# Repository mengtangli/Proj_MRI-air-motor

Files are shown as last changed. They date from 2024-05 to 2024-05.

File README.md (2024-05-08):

# Proj_MRI-air-motor
# readme

% ========================== GENERAL INFO ============================== %

 - Authors: Zhijie Pan & Mengtang Li, Ph.D.
 - Institution: Sun Yat-Sen University, China.
 - Date: 2024 05 08 (first release)

 Description:
  - Please read the published Journal ariticle for more info: Pan, Z., et al. Cornerstone for MRI-compatible robots: A continuous pneumatic actuator
with easy-to-connect prismatic/revolute and bidirectional encoder modules, MEASRUEMENT, 2024. https://doi.org/10.1016/j.measurement.2024.114685
  - Supp. Vid can be found at: https://www.youtube.com/watch?v=GabAmfBLwVU&t=7s
  - This guihub repo contains the open sourced CAD files for the proposed MRI-compatible pneumatic motor, and PCB files for the optical fiber encoder (will update later).

% ========================== Detailed INFO - ENG ============================== %
## Three-dimensional Design Software and Versions

SolidWorks Version: 2019 and above. Files cannot be opened in versions lower than this.

## Modification of Part Dimensions

Models in the `Vanetype_AirMotor_V2` folder are designed with perfect dimensions. However, due to manufacturing tolerances and assembly requirements, some parts need slight modifications.

Models in the `Vanetype_AirMotor_V2_prototype` folder account for manufacturing tolerances and assembly requirements. However, their accuracy depends on the precision of the 3D printer or CNC machine used. The "Parts list" file provides the types and quantities of parts needed to assemble the prototype.

The table below indicates key modifications made to parts in this prototype for reference only. Actual modifications should be based on the precision of your 3D printer and CNC machine.

| Part Name          |                           Modifications                           |
| :----------------- | :---------------------------------------------------------------: |
| output_shaft       |      Reduced the cylinder diameter for positioning planetary gears by 0.2mm, decreased disk thickness by 0.1mm      |
| carrier_thick      | Reduced the cylinder diameter for positioning planetary gears by 0.2mm, decreased disk thickness by 0.1mm, reduced thickness of middle gear by 0.2mm |
| carrier_thin       | Reduced the cylinder diameter for positioning planetary gears by 0.2mm, decreased disk thickness by 0.1mm, reduced thickness of middle gear by 0.2mm |
| input_gear         |                        Reduced thickness by 0.2mm                         |
| reducer_cover_back |                      Decreased disk thickness by 0.5mm                       |
| rotor              |          Increased blade slot width by 0.15mm, shortened output shaft length by 0.2mm           |
| motor_back_cover   |               Increased outer diameter of guide rail by 0.2mm, decreased inner diameter by 0.1mm               |
| motor_front_cover  |               Increased outer diameter of guide rail by 0.2mm, decreased inner diameter by 0.1mm               |
| motor_housing      |           Increased overall thickness by 0.3mm, enlarged diameter of middle through-hole by 0.2mm           |
| encoder_disk       |                      Reduced overall thickness by 0.2mm                       |

## Notes

- Due to frequent relative sliding between vanes, rotor, and two covers (motor_back_cover and motor_front_cover), it's recommended to use materials with low friction coefficients for these parts. Teflon material was used here, machined through CNC. Ensure smooth movement between these parts and apply plastic-specific lubricant if necessary.
- The sealing of the motor chamber significantly affects motor output performance. Here, two O-ring rubber seals are used to ensure the motor housing remains airtight.
- When the output shaft of the reducer experiences axial force, it significantly affects the torque performance of the actuator, as mentioned in the paper showing the performance graph with the linear module. This is likely due to the structure of the reducer, where axial pressure increases the resistance experienced by the input gear of the reducer, directly affecting rotor rotation.
- Plastic-specific lubricant should be added inside the reducer to reduce friction.
- Experimental testing revealed that the actuator prototype does not initially perform at its best. As the testing progresses and internal parts wear in over time, the performance of the actuator prototype improves.

% ========================== Detailed INFO - CHN ============================== %
## 三维制图软件及版本

SolidWorks版本：2019及以上，低于此版本则打不开SW源文件。

## 零件尺寸修改

`Vanetype_AirMotor_V2`文件夹中的模型为完美尺寸模型，由于需要考虑制造误差以及配合公差，因此需要对一些零件稍作修改。

`Vanetype_AirMotor_V2_prototype` 文件夹中的模型考虑了制造误差以及配合公差，由于3D打印和CNC加工的精度取决于所操作的机器，因此仅作参考。`Parts list`文件给出了制作样机所需要零件的种类及数量。

下表列举了本样机中的零件已修改了哪些关键的地方，仅作参考，需要根据自己的3D打印机和CNC机器的制造精度进行修改。

| 零件名称           |                           修改选型                           |
| :----------------- | :----------------------------------------------------------: |
| output_shaft       |      定位行星齿轮的圆柱直径减小0.2mm，圆盘厚度减小0.1mm         |
| carrier_thick      | 定位行星齿轮的圆柱直径减小0.2mm，圆盘厚度减小0.1mm，中间齿轮厚度减小0.2mm |
| carrier_thin       | 定位行星齿轮的圆柱直径减小0.2mm，圆盘厚度减小0.1mm，中间齿轮厚度减小0.2mm |
| input_gear         |                        厚度减小0.2mm                         |
| reducer_cover_back |                      圆盘厚度减小0.5mm                       |
| rotor              |          叶片槽宽度增加0.15mm，输出轴长度缩短0.2mm             |
| motor_back_cover   |               导轨外径增加0.2mm，内径减小0.1mm               |
| motor_front_cover  |               导轨外径增加0.2mm，内径减小0.1mm               |
| motor_housing      |           整体厚度增加0.3mm，中间通孔直径增大0.2mm            |
| encoder_disk       |                      整体厚度减小0.2mm                       |

## 注意事项

- 由于叶片 (vane) 与转子 (rotor)、叶片 (vane) 与两个封盖 (motor_back_cover and motor_front_cover) 之间存在频繁的相对滑动，因此建议使用摩擦系数低的材料制作这些零件，这里使用了特氟龙 (teflon)材料通过CNC加工得到。需要确保这些零件之间能够顺畅地滑动，必要时可添加塑料专用润滑脂。
- 马达 (motor) 腔室的密封性对马达的输出性能影响较大，这里通过两个O型弹性橡胶圈进行密封，确保马达外壳不会漏气。
- 减速器的输出轴受到轴向力时，会显著影响执行器的扭矩性能的输出，这点论文中在展示搭配直线模块性能图时有提及到。原因猜测应该与减速器的结构有关，受到轴向压力时，会增大减速器的输入齿轮所受到的阻力，从而直接影响转子转动。
- 减速器内部需要添加塑料专用的润滑脂，从而降低摩擦。
- 实验测试时发现，刚装配完成执行器样机并没有发挥出最好的性能，随着测试进行，内部零件磨合一段时间后，执行器样机的性能会提升。

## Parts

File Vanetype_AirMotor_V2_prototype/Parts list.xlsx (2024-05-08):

 | 零件名称 | 数量 | 备注
Motor | motor_back_cover | 1
 | rotor | 1
 | vane | 5
 | motor_housing | 1
 | motor_front_cover | 1
Encoder | encoder_support | 1
 | encoder_housing | 1
 | encoder_disk | 1
Reducer | reducer_housing | 1
 | reducer_housing_two-stage | 1
 | input_gear | 2
 | carrier_thin | 1
 | planet_gear_thin | 9
 | carrier_thick | 2
 | output_shaft | 2
 | planet_gear_thick | 6
 | reducer_cover_front | 2
 | reducer_cover_back | 2
Linear module | linear_main_housing | 1
 | linear_output_shaft | 1
 | rotation_screw | 1
Standard component | 塑料轴承
 | 5*11*3 | 2
 | 8*16*4 | 2
 | 3*7*2 | 1
 | 其他
 | Φ42*1.5 O型密封圈 | 2
 | M3*40螺丝 | 4
 | M3*12螺丝 | 4
 | M3*25螺丝 | 4
 | M2*12螺丝 | 4
 | M2.5*12尼龙平头螺丝 | 3
 | M2.5尼龙螺母 | 3
 | M3螺母 | 8

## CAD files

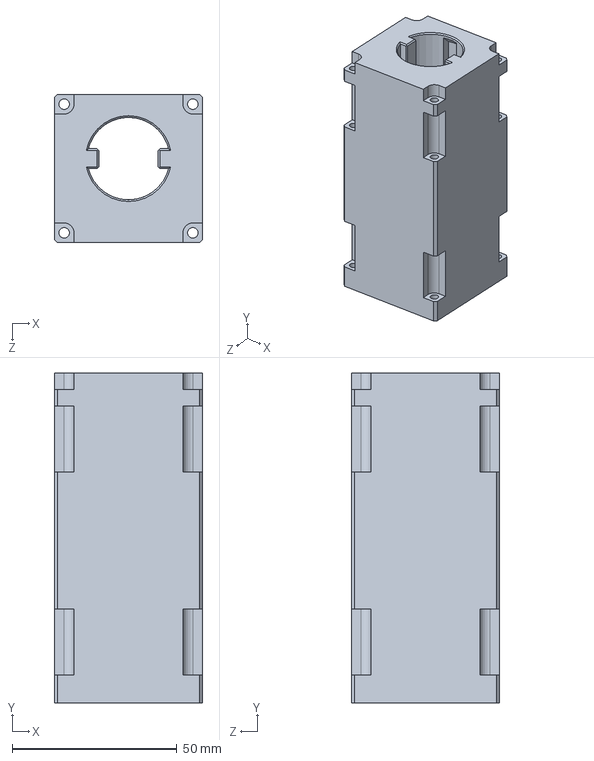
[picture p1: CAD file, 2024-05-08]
Vanetype_AirMotor_V2/Linear_module/linear_main_housing.SLDPRT
45.0 x 100.0 x 45.0 mm

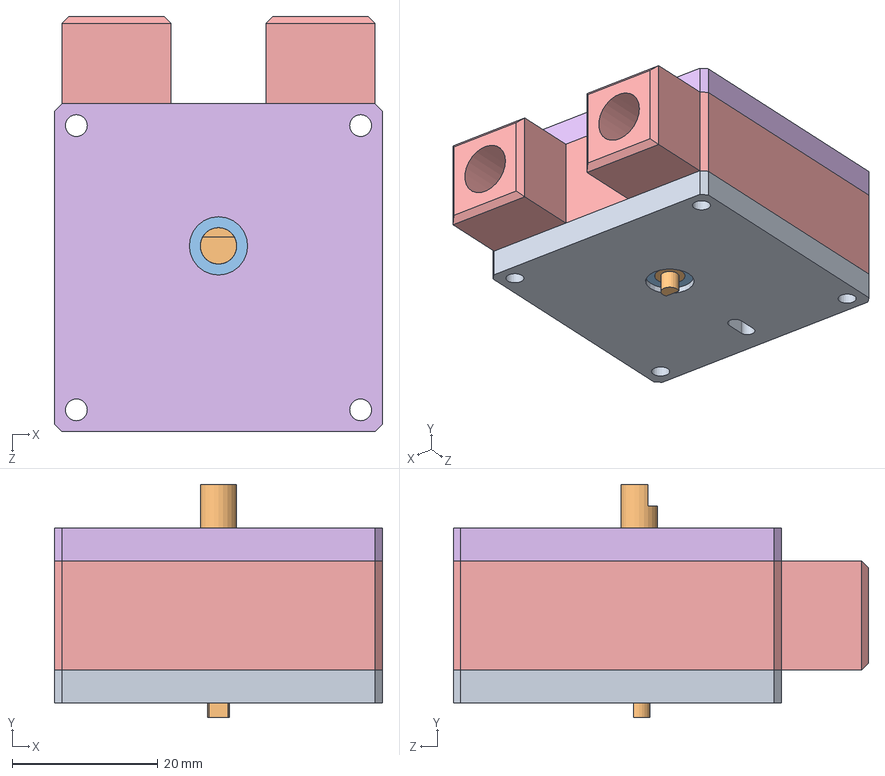
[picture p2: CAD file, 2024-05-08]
Vanetype_AirMotor_V2/Motor/motor.SLDASM
45.0 x 32.0 x 57.0 mm
motor_back_cover
rotor
5-11-3bearing x 2
vane x 5
motor_housing
motor_front_cover
sealing_ring x 2

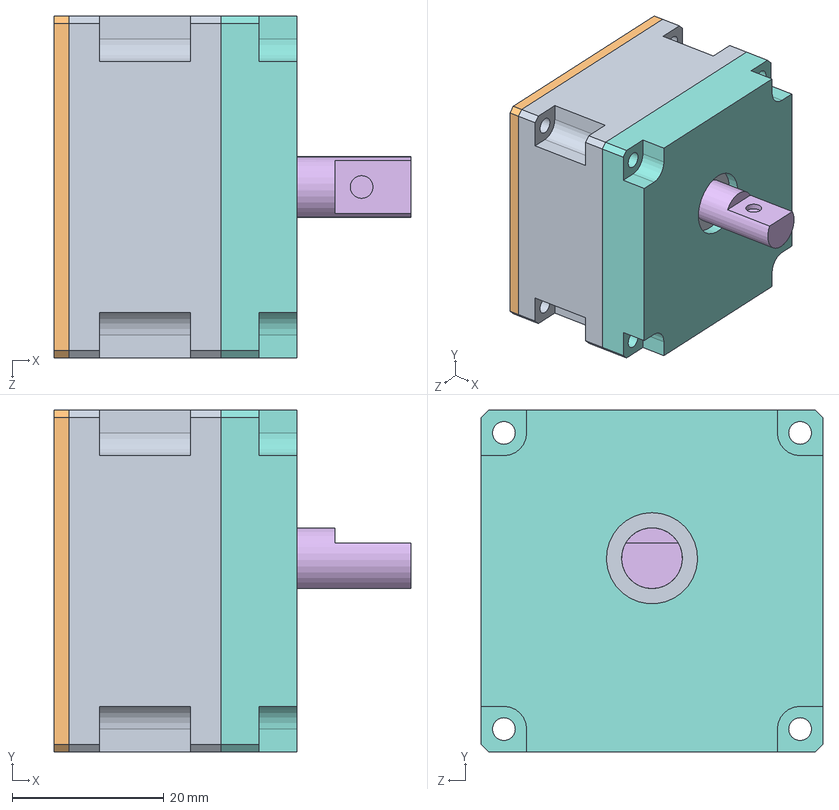
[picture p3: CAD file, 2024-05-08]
Vanetype_AirMotor_V2/Reducer/reducer.SLDASM
47.0 x 45.0 x 45.0 mm
reducer_housing
input_gear
carrier_thin
planet_gear_thin x 6
carrier_thick
output_shaft
planet_gear_thick x 3
reducer_cover_front
8-16-4bearing
reducer_cover_back

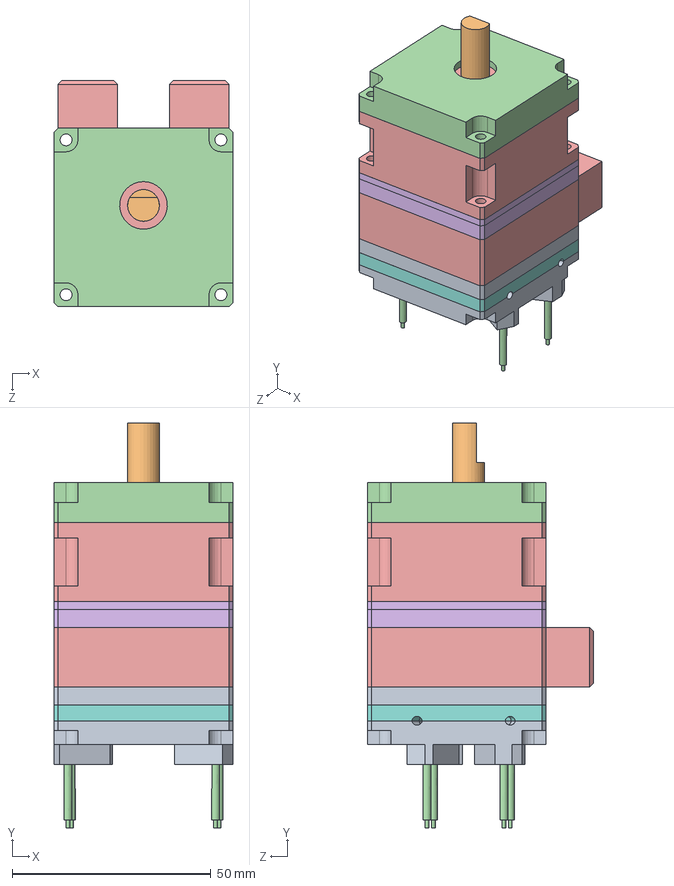
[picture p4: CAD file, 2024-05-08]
Vanetype_AirMotor_V2/Rotary_actuator.SLDASM
45.0 x 102.0 x 57.0 mm
motor_back_cover
rotor
5-11-3bearing x 2
vane x 5
motor_housing
motor_front_cover
sealing_ring x 2
encoder_support
encoder_housing
encoder_disk
3-7-2bearing
optical_fiber x 4
reducer_housing
input_gear
carrier_thin
planet_gear_thin x 6
carrier_thick
output_shaft
planet_gear_thick x 3
reducer_cover_front
8-16-4bearing
reducer_cover_back

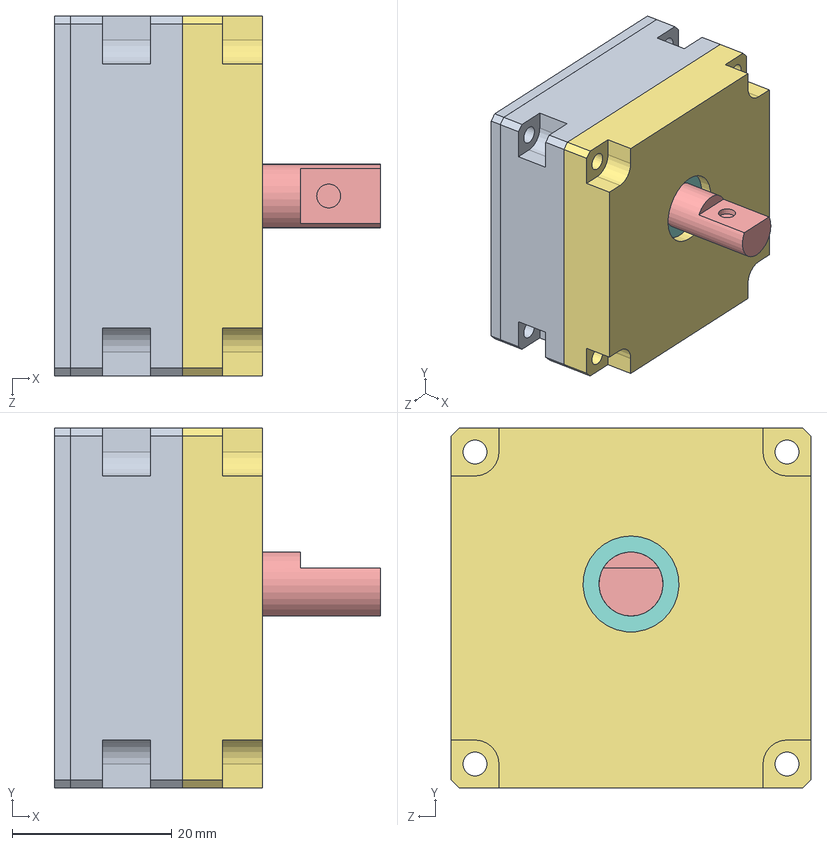
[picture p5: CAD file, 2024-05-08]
Vanetype_AirMotor_V2_prototype/Reducer/reducer_two-stage.SLDASM
40.8 x 45.0 x 45.0 mm
reducer_housing_two-stage
input_gear
carrier_thick
planet_gear_thin x 3
output_shaft
planet_gear_thick x 3
reducer_cover_front
8-16-4bearing
reducer_cover_back

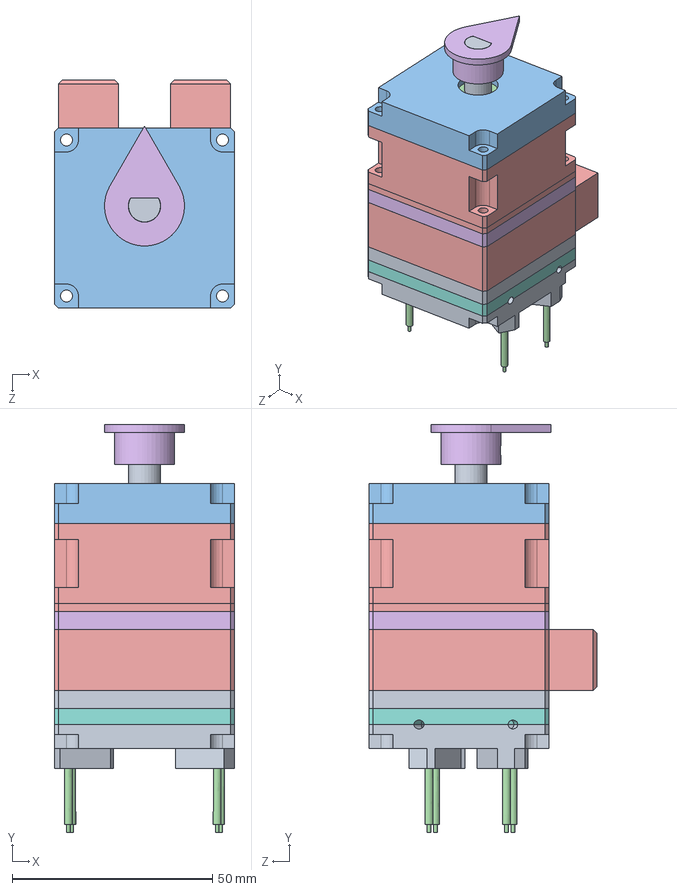
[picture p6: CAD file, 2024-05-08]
Vanetype_AirMotor_V2_prototype/Rotary_actuator_demonstrate.SLDASM
45.0 x 102.0 x 57.0 mm
motor_back_cover
rotor
5-11-3bearing x 2
vane x 5
motor_housing
motor_front_cover
sealing_ring x 2
encoder_support
encoder_housing
encoder_disk
3-7-2bearing
塑料光纤 x 4
reducer_housing
input_gear
carrier_thin
carrier_thick
output_shaft
planet_gear_thick x 3
reducer_cover_front
8-16-4bearing
reducer_cover_back
demonstra_part

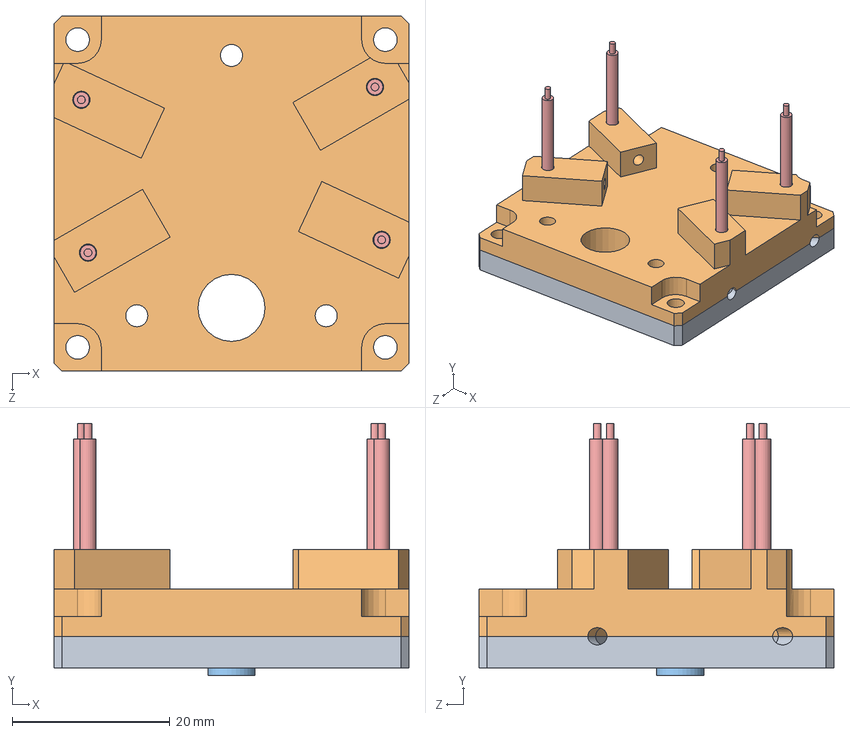
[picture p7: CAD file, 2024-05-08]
Vanetype_AirMotor_V2/Encoder/encoder.SLDASM
45.0 x 32.0 x 45.0 mm
encoder_support
encoder_housing
encoder_disk
3-7-2bearing
optical_fiber x 4

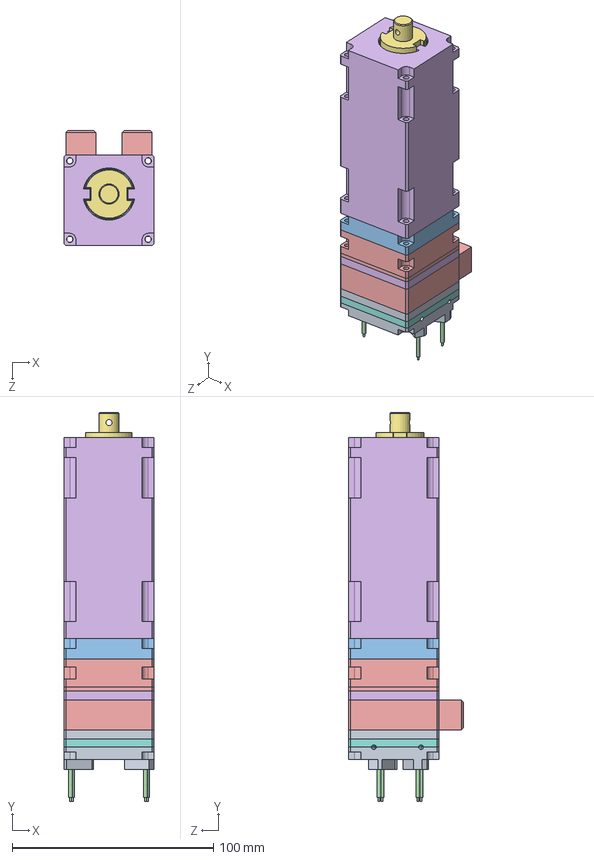
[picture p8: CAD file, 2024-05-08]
Vanetype_AirMotor_V2/Linear_actuator.SLDASM
45.0 x 193.5 x 57.0 mm
motor_back_cover
rotor
5-11-3bearing x 2
vane x 5
motor_housing
motor_front_cover
sealing_ring x 2
encoder_support
encoder_housing
encoder_disk
3-7-2bearing
optical_fiber x 4
reducer_housing_two-stage
input_gear
carrier_thick
planet_gear_thin x 3
output_shaft
planet_gear_thick x 3
reducer_cover_front
8-16-4bearing
reducer_cover_back
linear_main_housing
linear_output_shaft
rotation_screw

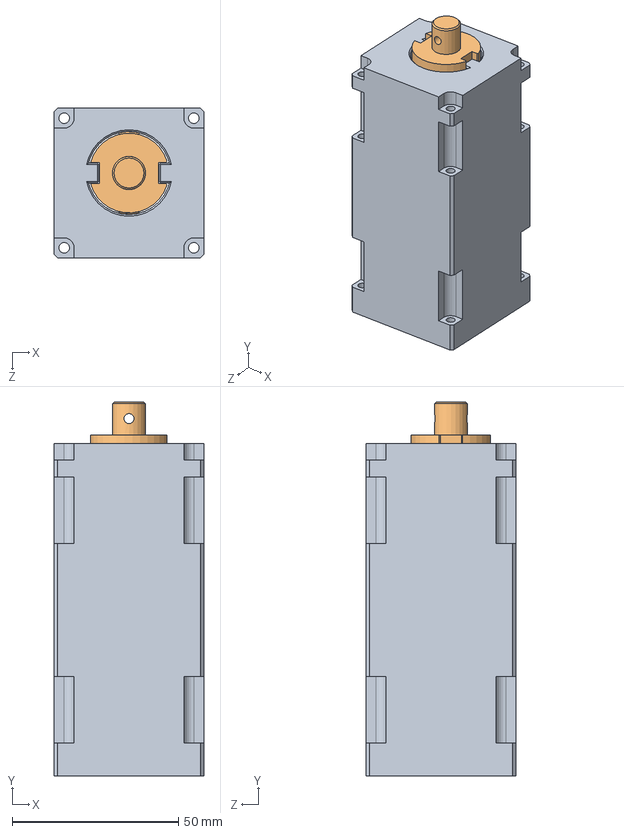
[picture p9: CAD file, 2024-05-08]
Vanetype_AirMotor_V2/Linear_module/Linear_converter.SLDASM
45.0 x 112.5 x 45.0 mm
linear_main_housing
linear_output_shaft
rotation_screw

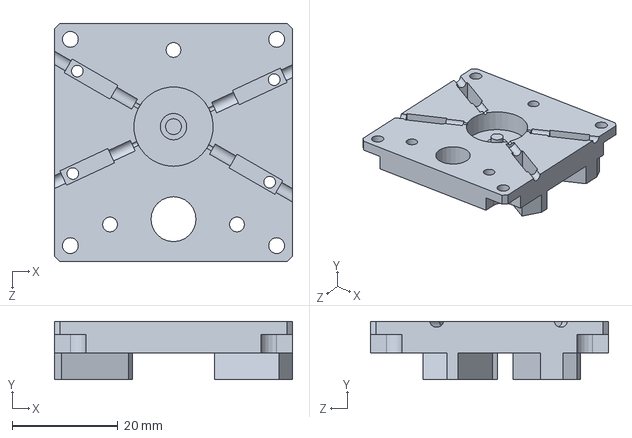
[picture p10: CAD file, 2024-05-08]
Vanetype_AirMotor_V2/Encoder/encoder_housing.SLDPRT
45.0 x 11.0 x 45.0 mm

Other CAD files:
Vanetype_AirMotor_V2_prototype/Motor/motor.SLDASM
Vanetype_AirMotor_V2/Reducer/reducer_two-stage.SLDASM
Vanetype_AirMotor_V2_prototype/Encoder/encoder.SLDASM
Vanetype_AirMotor_V2_prototype/Linear_actuator.SLDASM
Vanetype_AirMotor_V2_prototype/Linear_module/Linear_converter.SLDASM
Vanetype_AirMotor_V2_prototype/Reducer/reducer.SLDASM
Vanetype_AirMotor_V2_prototype/Rotary_actuator.SLDASM
Vanetype_AirMotor_V2/Encoder/3-7-2bearing.SLDPRT
Vanetype_AirMotor_V2/Encoder/encoder_disk.SLDPRT
Vanetype_AirMotor_V2/Encoder/encoder_support.SLDPRT
Vanetype_AirMotor_V2/Encoder/optical_fiber.SLDPRT
Vanetype_AirMotor_V2/Linear_module/linear_output_shaft.SLDPRT
Vanetype_AirMotor_V2/Linear_module/rotation_screw.SLDPRT
Vanetype_AirMotor_V2/Motor/5-11-3bearing.SLDPRT
Vanetype_AirMotor_V2/Motor/motor_back_cover.SLDPRT
Vanetype_AirMotor_V2/Motor/motor_cover.SLDPRT
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
